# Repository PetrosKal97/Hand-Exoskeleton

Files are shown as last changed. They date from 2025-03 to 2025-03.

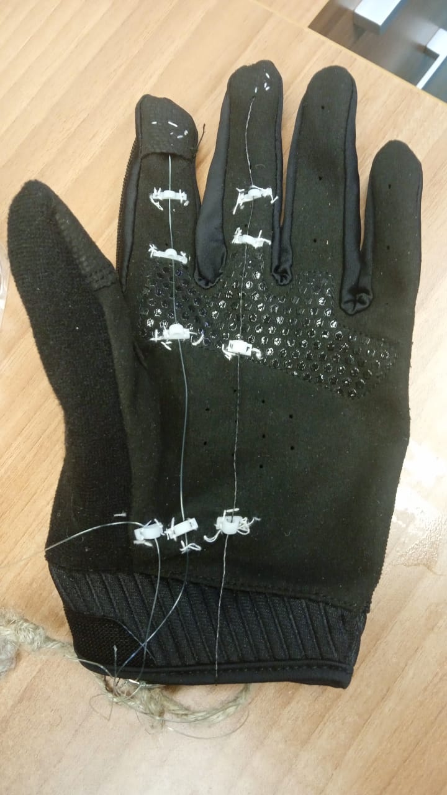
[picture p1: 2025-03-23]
Pictures/ glove.jpeg

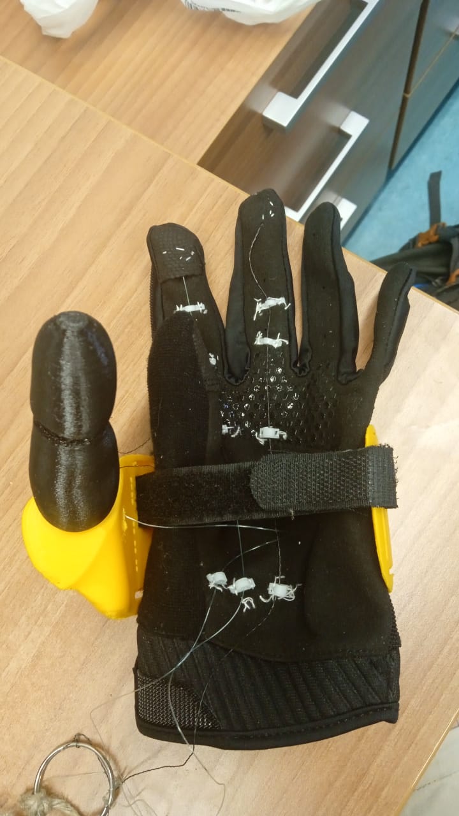
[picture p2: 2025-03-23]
Pictures/glove and splint.jpeg

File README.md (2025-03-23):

# Hand-Exoskeleton
An assistive technology for the handicapped.

The idea of the project is the development of a hand exoskeleton that would assist a patient with limited hand mobility to perform some basic grasps. 
The patient is a 60+ yo male, thumb amputee with zero or broken tendons on the fingers of his left hand. As a result, he can barely move some of his fingers. The movement of his wrist is weak and constrained.

A compliant structure in the form of a glove and tendons is preferred over rigid linkages as it simplifies the design process and makes the use by the patient more comfortable. 3D printed tendon guides are used to route the fishing lane, used as tendons, from the fingertip through the palm.

The proposed design is supposed to be fully body-powered, so it doesn't include any motors. Usually, body powered devices take advantage of the wrist flexion/extension to actuate the fingers, but the weak wrist of the patient does not give us this option. Alternatively, the elbow will be used. Another typical solution is shoulder. the folder "Previous devices:" includes some media from previous wrist actuated devices that were developed by the doctor and his team as well as some photos of patients.

To convert the motion of the elbow to a hand grasp, a tendon is anchored on a point somewhere on the patient's bicep. After passing through a guide mounted on the forearm of the patient, the tendon is connected to 5 different tendons that correspond to each finger. These finger tendons pass through some cable guides in the palm and the phalanxes of the fingers, before they get tied to an anchor point at the fingertip. This way, the patient can close his fingers by extending his elbow.

The tendon guides designed for the glove should not affect the grasping action. Especially the anchor points, are located on the fingertips which means that they interact a lot with the grasping object. Minimum interaction is recommended, since the glove or the fingertip itself offers much better friction characteristics useful in grasping. Location of the guides and anchor points is critical, since the kinematics of the fingers can dramatically change.

To replace the absence of the thumb, two different designs are proposed. "Thumb whole with hinge" is a one-part thumb, printed using TPU that is using the inner elasticity of TPU to form its joints. "Thumb bottom part" & "thumb top part" are two parts, printed in resin, of a solid thumb and are connected using hinges printed in TPU as joints. Both designs are mounted on a 3d printed splint, that is supposed to hug the back of the hand and offer stability to the prosthetic thumb. The splint and the glove are sewn together. The splint design can be found as "Splint"

To maintain the grasp, even when the patient's elbow is flexed, some latching mechanisms are proposed. "Linear latch" has the disadvantage that it needs to be more than double in length compared to the maximum travelling distance. "Rotating latch" needs calibration and scaling to match perfectly the travelling distance of the tendon. An exoskeleton developed by "openbionics" is using a latch mechanism that could be used and can be found [here](https://github.com/OpenBionics/Body-Powered-Exoskeleton-Glove).

A later upgrade, could be the addition of a mechanism that is delaying the closing of the fingers until the elbow is fully extended, in order to simplify grasping objects located a bit far from the patient's body, since otherwise the grasp is being performed gradually while the elbow is being extended.

***EXTRA DETAILS

 It is important to have a glove that fits the patient well and is from a material similar to lycra, in order to adapt to the hand of the patient.
 
 The connection of the splint and the glove can be performed with various ways, like sewing, or clamping.
 
 The length of the prosthetic thumb and its orientation can be modified to achieve better results. The same applies to the length of the hinges and in the infill percentage and pattern of the printed parts. The use of other materials is also possible.
 
 To avoid the interaction of the tendons and the velcro strap used on the splint, the velcro strap should pass through the inside of the glove under the tendons.
 
 The use of a differential, pretension or elastic tendons is also recommended to compensate for the differnt finger lengths.
 
 The splint used to fit the patient's hand is designed using the sculpting environment of Fusion. Other CAD softwares can also be used.
 
 ***

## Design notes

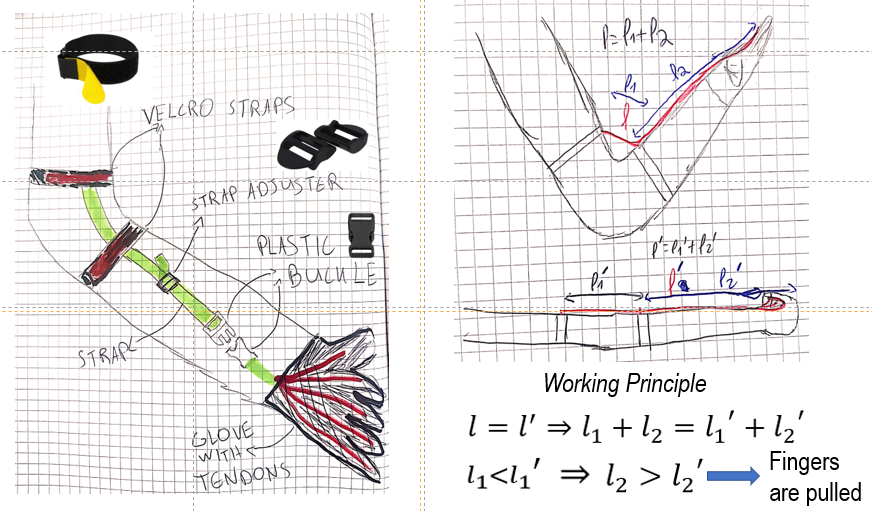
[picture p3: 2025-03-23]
working principle.png

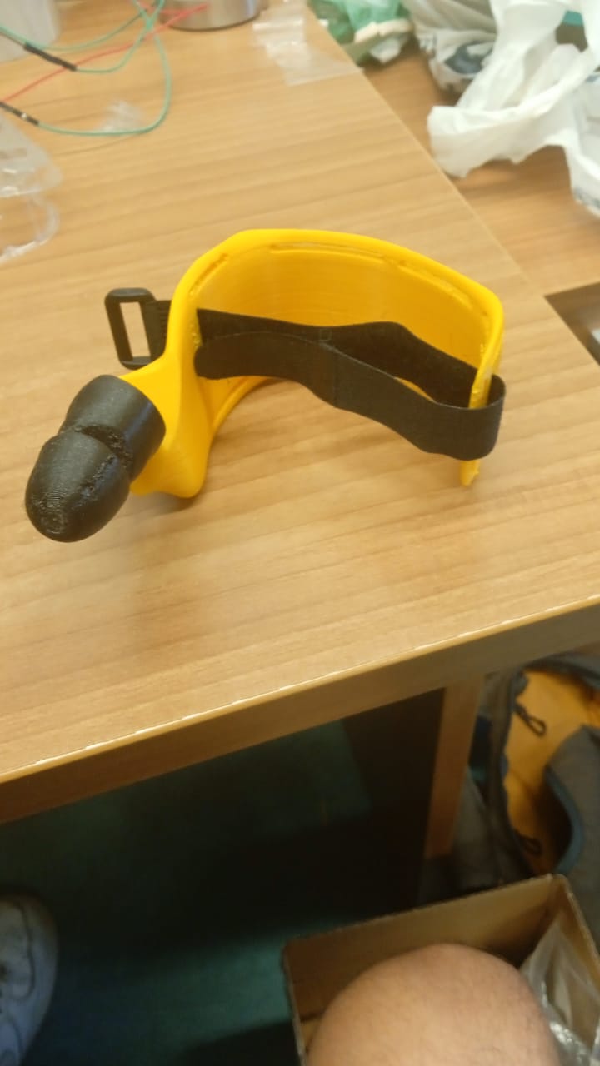
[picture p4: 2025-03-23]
Pictures/ splint & thumb.jpeg

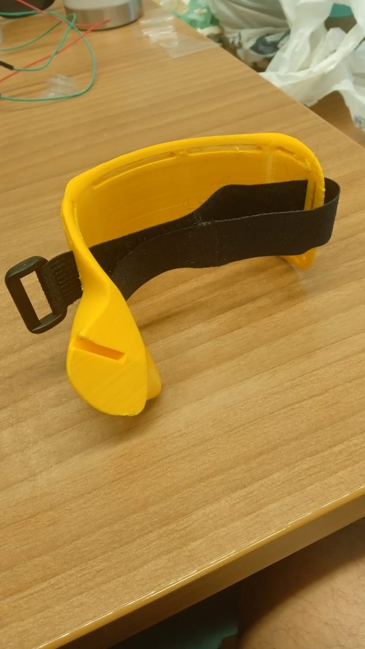
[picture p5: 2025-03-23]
Pictures/ splint.jpeg

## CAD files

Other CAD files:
STL files /latching mechanisms/ rotating latch.f3d
Thumb & splint designs/Hinges/hinge .f3d
Thumb & splint designs/Hinges/hinge 2.f3d
Thumb & splint designs/Hinges/hinge 3.f3d
Thumb & splint designs/Hinges/hinge 4.f3d
Thumb & splint designs/thumb bottom part.f3d
Thumb & splint designs/thumb top part.f3d
Thumb & splint designs/thumb whole with hinge.f3d
latching mechanisms/ rotating latch.f3d
latching mechanisms/linear latch.f3d
tendon guides/ palm guide.f3d
tendon guides/ phalanx guide curve.f3d
tendon guides/ phalanx guide straight.f3d
tendon guides/anchor point finger.f3d

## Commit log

2025-03-23 Rename linear latch.f3d to latching mechanisms/linear latch.f3d
    [linear latch.f3d]
2025-03-23 Rename anchor point finger.f3d to latching mechanisms/ anchor point finger.f3d
    [anchor point finger.f3d]
2025-03-23 Rename anchor point finger.f3d to anchor point finger.f3d
    [anchor point finger.f3d]
2025-03-23 Rename palm guide.f3d to tendon guides/ palm guide.f3d
    [palm guide.f3d]
2025-03-23 Rename phalanx guide curve.f3d to tendon guides/ phalanx guide curve.f3d
    [phalanx guide curve.f3d]
2025-03-23 Rename phalanx guide straight.f3d to tendon guides/ phalanx guide straight.f3d
    [phalanx guide straight.f3d]
2025-03-23 Rename rotating latch.f3d to latching mechanisms/ rotating latch.f3d
    [rotating latch.f3d]
2025-03-23 Rename latching mechanisms/ rotating latch.f3d to STL files /latching mechanisms/ rotating latch.f3d
    [rotating latch.f3d]
2025-03-23 Rename STL files /latching mechanisms/ rotating latch.f3d to latching mechanisms/ rotating latch.f3d
    [rotating latch.f3d]
2025-03-23 Rename splint.f3d to Thumb & splint designs/ splint.f3d
    [splint.f3d, splint.f3d]
2025-03-23 Rename Thumb & splint designs/hinge .f3d to Thumb & splint designs/Hinges/hinge .f3d
    [hinge .f3d]
